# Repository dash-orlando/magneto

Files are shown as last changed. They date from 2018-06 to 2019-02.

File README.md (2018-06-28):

# magneto
PD3D Original Project: El Magnito Bandito

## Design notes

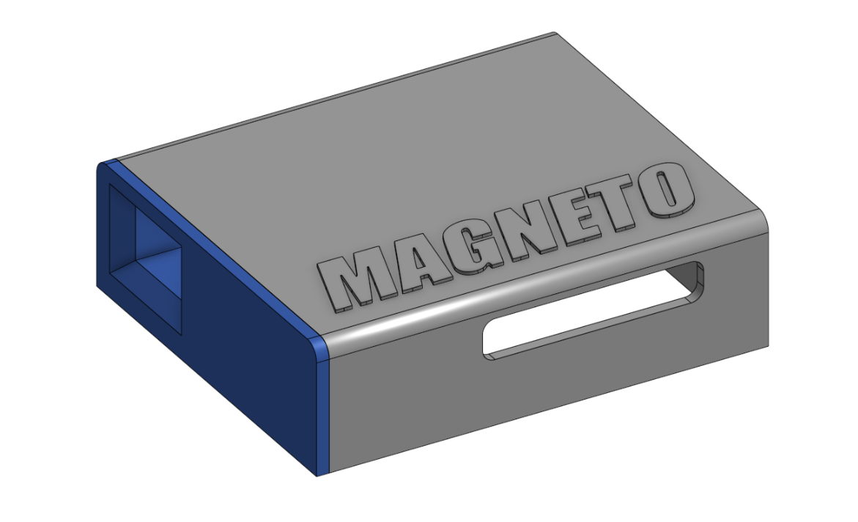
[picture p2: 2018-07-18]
Hardware/wearables/necklace/box/electronics_box_v1.png

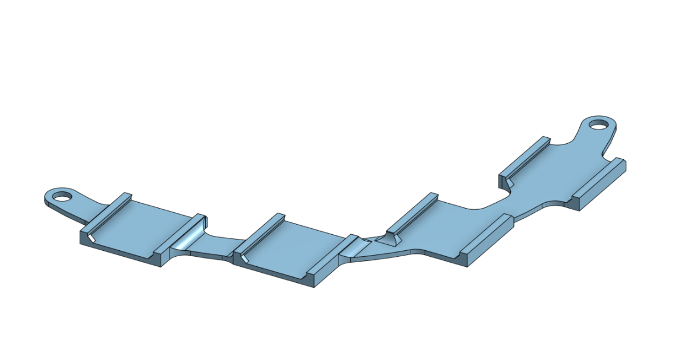
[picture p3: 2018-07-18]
Hardware/wearables/necklace/array/tunable_sensor_array_v1.png

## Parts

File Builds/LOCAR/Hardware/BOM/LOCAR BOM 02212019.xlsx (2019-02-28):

Part | Description |  | Source | Count | Price/unit
LED NeoPixel 12x5050 | Natural White LED ring for "Endoscope" |  | https://www.adafruit.com/product/2853 | 0 | $9.50
Rasberry Pi 3A+ | Controller for Magnetic Array |  | https://www.canakit.com/raspberry-pi-3-model-a-plus.html?cid=usd&src=raspberrypi | 0 | $25
Pi Camera | For "Laparoscope" |  | https://www.amazon.com/Raspberry-Pi-Camera-Module-Megapixel/dp/B01ER2SKFS?s=electronics | 0 | $24.90
Pi Camera Extension Cable | 1 meter |  | https://www.adafruit.com/product/2143 | 0 | $3.95
Power Supply | 5V 10A |  | https://www.amazon.com/dp/B00J3MHTYG/ref=nav_timeline_asin?_encoding=UTF8&th=1 | 2 | $10.99
M3 Inserts | 240-M3-BR M3-0.5 |  | https://www.amazon.com/240-M3-BR-M3-0-5-Flush-Press-Insert/dp/B06XGXFM21 | 1 | $14.50
10.1" Screen | for RAPID |  | https://www.amazon.com/Raspberry-Screen-10-1-IPS-SunFounder/dp/B07FZZ95WN?s=electronics | 1 | $110.00
Power Supply | 500W+ ATX style power supply | Needed to power the LOCAR | https://www.amazon.com/Corsair-Bronze-Certified-Modular-CP-9020102-NA/dp/B01B72W0A2 | 1.00 | $59.99

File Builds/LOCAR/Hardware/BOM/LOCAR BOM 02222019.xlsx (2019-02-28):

Account PI | Account Number | Project | Part | Description | Justification | Source | Count | Price/unit
Fluvio Lobo | 64018456 | EMGF - PCD | LED NeoPixel 12x5050 | Natural White LED ring for "Endoscope" |  | https://www.adafruit.com/product/2853 | 0.00 | $9.50 | $0.00
Fluvio Lobo | 64018456 | EMGF - PCD | Rasberry Pi 3A+ | Controller for Magnetic Array |  | https://www.canakit.com/raspberry-pi-3-model-a-plus.html?cid=usd&src=raspberrypi | 0.00 | $25.00 | $0.00
Fluvio Lobo | 64018456 | EMGF - PCD | Mount for 7" Touchscreen |  |  | https://www.amazon.com/Case-Official-Raspberry-Touchscreen-Display/dp/B01HV97F64 | 0.00 | $27.99 | $0.00
Fluvio Lobo | 64018456 | EMGF - PCD | Pi Camera | For "Laparoscope" |  | https://www.amazon.com/Raspberry-Pi-Camera-Module-Megapixel/dp/B01ER2SKFS?s=electronics | 0.00 | $24.90 | $0.00
Fluvio Lobo | 64018456 | EMGF - PCD | Pi Camera Extension Cable | 1 meter |  | https://www.adafruit.com/product/2143 | 0.00 | $3.95 | $0.00
Fluvio Lobo | 64018456 | EMGF - PCD | Power Supply | 5V 10A |  | https://www.amazon.com/dp/B00J3MHTYG/ref=nav_timeline_asin?_encoding=UTF8&th=1 | 0.00 | $10.99 | $0.00
Fluvio Lobo | 64018456 | EMGF - PCD |  |  |  |  |  |  | $0.00
Fluvio Lobo | 64018456 | EMGF - PCD | Power Supply | 500W+ ATX style power supply | Needed to power the LOCAR | https://www.amazon.com/Corsair-Bronze-Certified-Modular-CP-9020102-NA/dp/B01B72W0A2 | 1.00 | $59.99 | $59.99
Fluvio Lobo | 64018456 | EMGF - PCD | Power Dist. PCB | Custom PCB for power distribution | Needed to distribute power to each individual LOCAR component | Oshpark | 0.00 | $20.00 | $0.00
Fluvio Lobo | 64018456 | EMGF - PCD | Power Supply Cable | ATX Power Supply Connector - Right angle THT | Needed to assemble Power Dist. PCB | https://www.amazon.com/ATX-Power-Supply-Connector-Right/dp/B004G4ZFY2 | 4.00 | $2.95 | $11.80
Fluvio Lobo | 64018456 | EMGF - PCD | M3 Inserts | 240-M3-BR M3-0.5 |  | https://www.amazon.com/240-M3-BR-M3-0-5-Flush-Press-Insert/dp/B06XGXFM21 | 1.00 | $14.50 | $14.50
Fluvio Lobo | 64018456 | EMGF - PCD | 10.1" Screen | Raspberry Pi Screen | Needed to interface the Pi OS | https://www.amazon.com/Raspberry-Screen-10-1-IPS-SunFounder/dp/B07FZZ95WN?s=electronics | 1.00 | $110.00 | $110.00
Fluvio Lobo | 64018456 | EMGF - PCD | Plastic Spool | White | Needed to print parts | https://www.amazon.com/HATCHBOX-3D-Filament-Dimensional-Accuracy/dp/B00J0GMMP6?hvadid=312157487430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 | 1.00 | $20.00 | $20.00
Fluvio Lobo | 64018456 | EMGF - PCD | Plastic Spool | Silver | Needed to print parts | https://www.amazon.com/HATCHBOX-3D-Filament-Dimensional-Accuracy/dp/B00J0ECR5I | 1.00 | $20.00 | $20.00
Fluvio Lobo | 64018456 | EMGF - PCD | Plastic Spool | Black | Needed to print parts | https://www.amazon.com/HATCHBOX-3D-Filament-Dimensional-Accuracy/dp/B00MEZEEJ2?s=industrial | 1.00 | $20.00 | $20.00
 |  |  |  |  |  |  |  | Total = | $216.29

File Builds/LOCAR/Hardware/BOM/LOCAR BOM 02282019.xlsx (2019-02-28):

Part | Description | Justification | Source | Count | Price/unit
Right Angle Male Pins | Right Angle Male Pins | Needed to assemble the daisy-hub modules | https://www.amazon.com/Simpo-2-54mm-Connector-Plastic-Gold-plated/dp/B07BRZC6C6?hvadid=241935719665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 | 2.00 | $14.99 | $29.98
Female Header Pins | Female Header Pins | Needed to stack daisy-hub prototypes | https://www.amazon.com/Hilitchi-2-54mm-Arduino-Stackable-Assortment/dp/B01IPA8JZY?s=gateway | 2.00 | $9.99 | $19.98
 |  |  |  |  | Total = | $49.96

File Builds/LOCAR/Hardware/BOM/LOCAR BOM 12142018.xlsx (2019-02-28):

Part | Description | Justification | Source | Count | Price/unit
LED NeoPixel 12x5050 | Natural White LED ring for "Endoscope" |  | https://www.adafruit.com/product/2853 | 2.00 | $9.50 | $19.00
Rasberry Pi 3A+ | Controller for Magnetic Array |  | https://www.canakit.com/raspberry-pi-3-model-a-plus.html?cid=usd&src=raspberrypi | 3.00 | $25.00 | $75.00
Mount for 7" Touchscreen |  |  | https://www.amazon.com/Case-Official-Raspberry-Touchscreen-Display/dp/B01HV97F64 | 2.00 | $27.99 | $55.98
Pi Camera | For "Laparoscope" |  | https://www.amazon.com/Raspberry-Pi-Camera-Module-Megapixel/dp/B01ER2SKFS?s=electronics | 2.00 | $24.90 | $49.80
Pi Camera Extension Cable | 1 meter |  | https://www.adafruit.com/product/2143 | 2.00 | $3.95 | $7.90
Power Supply | 5V 10A |  | https://www.amazon.com/dp/B00J3MHTYG/ref=nav_timeline_asin?_encoding=UTF8&th=1 | 2.00 | $10.99 | $21.98
 |  |  |  |  |  | $0.00
Power Supply | 500W+ ATX style power supply | Needed to power the LOCAR | https://www.amazon.com/Corsair-Bronze-Certified-Modular-CP-9020102-NA/dp/B01B72W0A2 | 1.00 | $59.99 | $59.99
Power Dist. PCB | Custom PCB for power distribution | Needed to distribute power to each individual LOCAR component | Oshpark | 1.00 | $20.00 | $20.00
 | ATX Power Supply Connector - Right angle THT | Needed to assemble Power Dist. PCB | https://www.amazon.com/ATX-Power-Supply-Connector-Right/dp/B004G4ZFY2 | 1.00 | $2.95 | $2.95
 |  |  |  |  | Total = | $312.60

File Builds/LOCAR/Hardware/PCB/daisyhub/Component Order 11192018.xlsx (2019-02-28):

Account PI | Account Number | Account Name | Component | ID | Description | Justification | Link | Unit Cost | Quantity | Total Cost | Ordered | Delivered
Jack Stubbs |  |  | Jumper Cables |  | 4 pin, female to female jumper cables | Needed to connect daisy-pair modules | https://www.amazon.com/FEBNISCTE-Female-Jumper-Cable-Printer/dp/B00KWA1UWK?s=electronics | $9.99 | 2.00 | $19.98
 |  |  | Female Headers |  | Assortment of female headers | Needed to connect IMUs at certain height | https://www.amazon.com/Glarks-Connector-Assortment-Stackable-Breakaway/dp/B07CWSXY7P?s=electronics | $12.85 | 2.00 | $25.70
 |  |  | Right-angle, male headers |  | Right-angle | Needed to connect IMU pair modules | https://www.amazon.com/Saim-10PCS-2-54mm-Single-Headers/dp/B00899WOXK?s=electronics | $5.55 | 2.00 | $11.10
 |  |  | Straight, male headers |  | Straight | Needed to connect IMUs close to the surface of the breakout | https://www.amazon.com/Breakaway-Header-Straight-Connector-Prototype/dp/B07BXDYTBP?s=electronics | $8.99 | 1.00 | $8.99
 |  |  | LED |  | 5V, 3 mm |  | https://www.mouser.com/ProductDetail/Kingbright/WP710A10ID5V | $0.41 | 25.00 | $10.35
 |  |  | LED |  | 5V, 3 mm |  | https://www.mouser.com/ProductDetail/?qs=jBF9H7RTBaQ2jkR1uoa79Q%3d%3d | $0.41 | 25.00 | $10.35
 |  |  | LED |  | 5V, 3 mm |  | https://www.mouser.com/ProductDetail/Kingbright/WP710A10YD5V | $0.41 | 25.00 | $10.35
 |  |  |  |  |  |  |  |  | Total | $96.82

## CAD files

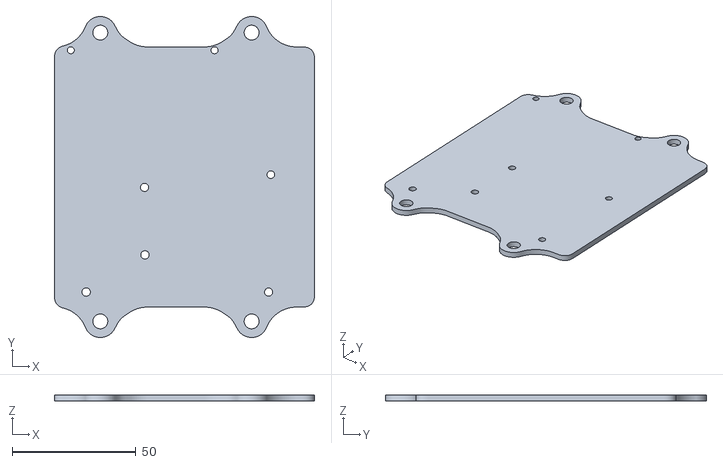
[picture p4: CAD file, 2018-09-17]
Builds/LOCAR/Hardware/6MAG_arduino_plate.stl
105.0 x 129.5 x 2.50

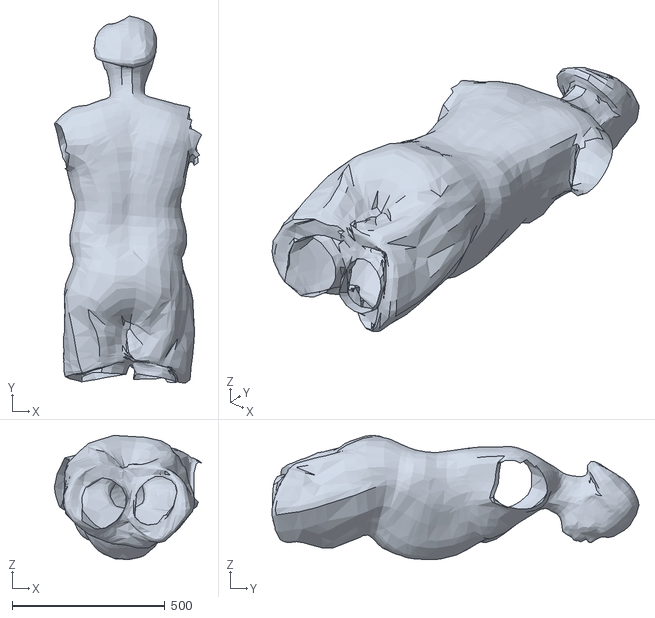
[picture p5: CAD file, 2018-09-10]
Builds/LOCAR/Software/Windows/Python 2.7/SP_PH02_Torso.obj
482.9 x 1202.6 x 406.8

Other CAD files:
Software/Python/Steth Edition/SP_PH02_Torso_Inverted (ASCII).stl
Builds/LOCAR/Software/Windows/Python 2.7/SP_PH02_Torso (BIN).stl
Builds/LOCAR/Software/Windows/Python 2.7/SP_PH02_Torso (ASCII).stl

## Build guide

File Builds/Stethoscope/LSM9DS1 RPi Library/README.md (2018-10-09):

SparkFun LSM9DS1 RaspberryPI Library
===

68747470733a2f2f63646e2e737061726b66756e2e636f6d2f2f6173736574732f70617274732f312f302f352f332f332f31333238342d30322e6a7067

[LSM9DS1 Breakout Board (SEN-13284)](https://www.sparkfun.com/products/13284)

Port [SparkFun_LSM9DS1_Arduino_Library](https://github.com/sparkfun/SparkFun_LSM9DS1_Arduino_Library) to Raspberry Pi

This library supports only I2C.

## Requirement

* [WiringPi](http://wiringpi.com/)

## Install

```
$ git clone https://github.com/akimach/LSM9DS1_RaspberryPi_Library.git
$ cd LSM9DS1_RaspberryPi_Library
$ make
$ sudo make install
```

## Python example

```
$ cd ./example
$ sudo python LSM9DS1_Basic_I2C.py
```

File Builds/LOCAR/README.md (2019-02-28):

# LOCAR
_**LOCAR**_, or the _**Location-based Trocar or Laparoscopic Trainer**_, is a cost-effective system for the live position tracking of surgical end-effectors.

> **NOTE** The latest versions of **LOCAR** are located in the _**locar**_ branch of the _**magneto**_ repository

## INSTALLATION
### Python 2.7
1. Install the following requirements
```
sudo pip install numpy
sudo pip install scipy
sudo apt-get install python-scipy
```

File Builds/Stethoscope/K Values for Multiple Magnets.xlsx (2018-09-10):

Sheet: Big Magnet
BIG MAGNET
H^2 | x | K | Hy^2 | y | K
6.86 | 0.075 | 1.220932617e-06 | 6.8121 | 0.075 | 1.212407446e-06
2.87 | 0.085 | 1.08241911e-06 | 2.8561 | 0.085 | 1.077176732e-06
1.31 | 0.095 | 9.629703767e-07 | 1.2769 | 0.095 | 9.386388351e-07
Taking Entire Norm |  | 1.088774035e-06 | Setting Hx=Hz=0 |  | 1.076074338e-06

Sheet: Small Magnet
SMALL MAGNET
H_x | H_y | H_z | x | y | z
0.19 | 0 | 0.83 | 0 | 0.075 | 0
K-Value |  |  |  |  | 1.290344238e-07

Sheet: Spherical Magnet
SPEHRICAL MAGNET
H^2 | x | K | Hy^2 | y | K
0.995 | 0.075 | 1.77088623e-07 | 0.996004 | 0.075 | 1.772673135e-07
0.64 | 0.085 | 2.4137569e-07 | 0.633616 | 0.085 | 2.389679675e-07
0.435 | 0.095 | 3.197649724e-07 | 0.42575625 | 0.095 | 3.129699668e-07
Taking Entire Norm |  | 2.460764285e-07 | Setting Hx=Hz=0 |  | 2.430684159e-07

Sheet: Small Magnet (with hole)
SMALL MAGNET (W\HOLE)
H_x | H_y | H_z | x | y | z
0.07 | 0.07 | 1.02 | 0 | 0.075 | 0
K-Value |  |  |  |  | 1.869130371e-07

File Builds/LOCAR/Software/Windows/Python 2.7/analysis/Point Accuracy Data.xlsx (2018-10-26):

 | Xm | Ym | Zm | Xe | Ye | Ze | Length | milliseconds to solution
No Tool | 11.791 | -135.68 | -430.562 | 3.488 | -40.137 | -127.368 | 318 | 0.021
 | 44.026 | -205.633 | -411.084 | 13.706 | -64.017 | -127.977 | 318 | 0.046
 | 13.39 | -262.575 | -389.993 | 4.337 | -85.047 | -126.316 | 318 | 0.05
 | 73.483 | -68.387 | -435.096 | 21.151 | -19.684 | -125.236 | 318 | 0.053
 | -8.5 | -55.943 | -457.334 | -2.634 | -17.338 | -141.74 | 318 | 0.05
 | 118.128 | -221.371 | -396.837 | 38.119 | -71.436 | -128.058 | 318 | 0.051
 | 35.189 | -392.242 | -217.09 | 10.305 | -114.866 | -63.574 | 318 | 0.052
 | 53.69 | -323.923 | -324.836 | 16.725 | -100.902 | -101.186 | 318 | 0.05
 | 0.882 | -297.198 | -345.54 | 0.267 | -89.837 | -104.449 | 318 | 0.049
 | -48.98 | -313.519 | -323.668 | -14.617 | -93.564 | -96.593 | 318 | 0.05
 | -40.418 | -106.73 | -450.539 | -12.764 | -33.704 | -142.275 | 318 | 0.05
 | 11.521 | 70.356 | -437.562 | 3.257 | 19.89 | -123.701 | 318 | 0.049
 | -41.873 | -323.034 | -334.576 | -13.357 | -103.045 | -106.726 | 318 | 0.05
 | 72.113 | -103.806 | -436.701 | 21.672 | -31.196 | -131.239 | 318 | 0.05
 | -40.18 | -152.054 | -449.781 | -13.364 | -50.575 | -149.603 | 318 | 0.052
 | 88.244 | -92.452 | -432.499 | 26.022 | -27.262 | -127.535 | 318 | 0.044
 | -129.119 | -84.686 | -421.646 | -37.678 | -24.712 | -123.04 | 318 | 0.047
 | -106.666 | -119.185 | -429.583 | -32.669 | -36.503 | -131.569 | 318 | 0.047
 | -78.684 | -142.069 | -418.498 | -22.945 | -41.428 | -122.037 | 318 | 0.045
 | 32.752 | -72.097 | -435.967 | 9.247 | -20.355 | -123.087 | 318 | 0.05
 | 15.918 | -112.405 | -428.539 | 4.5 | -31.776 | -121.143 | 318 | 0.043
 | 22.485 | -226.434 | -381.124 | 6.377 | -64.216 | -108.086 | 318 | 0.049
 | 43.544 | 30.685 | -435.418 | 11.978 | 8.441 | -119.772 | 318 | 0.046
 | -29.896 | -316.387 | -335.349 | -9.319 | -98.619 | -104.529 | 318 | 0.048
 | -13.988 | -355.039 | -281.021 | -4.169 | -105.814 | -83.754 | 318 | 0.045
 | -2.207 | -177.358 | -429.925 | -0.698 | -56.088 | -135.96 | 318 | 0.046
 | 11.226 | -145.789 | -431.476 | 3.39 | -44.026 | -130.3 | 318 | 0.047
 | -15.919 | -187.24 | -416.46 | -4.839 | -56.92 | -126.602 | 318 | 0.045
 | 30.017 | -122.881 | -426.986 | 8.582 | -35.134 | -122.084 | 318 | 0.048
 | 111.89 | -64.447 | -416.042 | 30.211 | -17.401 | -112.333 | 318 | 0.048
 | 93.979 | 47.633 | -426.244 | 25.914 | 13.134 | -117.535 | 318 | 0.046
 | 144.263 | 64.079 | -420.36 | 42.095 | 18.698 | -122.658 | 318 | 0.047
 | 128.704 | 20.196 | -435.387 | 38.646 | 6.064 | -130.733 | 318 | 0.046
 | 35.203 | 5.691 | -433.853 | 9.487 | 1.534 | -116.922 | 318 | 0.045
 | 23.279 | -101.283 | -434.158 | 6.697 | -29.136 | -124.894 | 318 | 0.047
 | -81.417 | -126.108 | -424.124 | -23.87 | -36.973 | -124.345 | 318 | 0.044
 | -40.877 | -148.342 | -435.77 | -12.749 | -46.267 | -135.914 | 318 | 0.045
 | 27.348 | -183.169 | -416.475 | 8.268 | -55.376 | -125.909 | 318 | 0.047
 | -46.981 | -42.877 | -442.12 | -13.534 | -12.351 | -127.361 | 318 | 0.048
 | -24.726 | -145.052 | -440.523 | -7.797 | -45.737 | -138.904 | 318 | 0.046
 | -54.388 | -166.254 | -413.258 | -15.847 | -48.442 | -120.412 | 318 | 0.047
 | 38.589 | -37.22 | -437.32 | 10.737 | -10.356 | -121.683 | 318 | 0.046
 | 2.676 | -139.262 | -422.801 | 0.764 | -39.779 | -120.768 | 318 | 0.047
 | 114.945 | -12.355 | -423.011 | 31.592 | -3.396 | -116.26 | 318 | 0.046
 | 2.491 | -86.519 | -417.186 | 0.632 | -21.945 | -105.817 | 318 | 0.046
 | 207.918 | -177.162 | -350.607 | 59.157 | -50.406 | -99.755 | 318 | 0.047
 | 152.829 | -13.231 | -409.746 | 41.749 | -3.614 | -111.933 | 318 | 0.046
 | 67.892 | -245.57 | -367.578 | 19.619 | -70.964 | -106.223 | 318 | 0.046
 | 28.39 | -126.567 | -420.371 | 7.868 | -35.079 | -116.508 | 318 | 0.047
 | 44.255 | -243.541 | -364.31 | 12.303 | -67.706 | -101.28 | 318 | 0.047
 | -5.605 | -289.303 | -331.712 | -1.556 | -80.302 | -92.074 | 318 | 0.046
 | -52.69 | -193.19 | -397.328 | -15.032 | -55.115 | -113.354 | 318 | 0.047
 | -100.554 | -233.97 | -367.093 | -28.983 | -67.439 | -105.81 | 318 | 0.047
 | -81.167 | -269.308 | -348.019 | -23.485 | -77.922 | -100.697 | 318 | 0.047
 | -87.173 | -258.012 | -350.972 | -24.772 | -73.32 | -99.737 | 318 | 0.045
 | -124.527 | -234.581 | -349.305 | -34.283 | -64.581 | -96.165 | 318 | 0.047
 | -100.678 | -315.033 | -275.066 | -26.252 | -82.146 | -71.724 | 318 | 0.047
 | -158.434 | -283.69 | -282.454 | -41.413 | -74.153 | -73.83 | 318 | 0.045
 | 42.369 | -398.35 | -115.912 | 10.061 | -94.593 | -27.525 | 318 | 0.048
 | 39.308 | -204.708 | -407.183 | 11.982 | -62.399 | -124.118 | 318 | 0.044
 | 57.747 | -130.26 | -438.532 | 17.921 | -40.425 | -136.096 | 318 | 0.046
 | 68.268 | -105.048 | -432.185 | 20.023 | -30.81 | -126.758 | 318 | 0.044
 | -25.019 | -134.94 | -431.035 | -7.431 | -40.079 | -128.023 | 318 | 0.048
 | 57.342 | -132.649 | -442.513 | 18.171 | -42.034 | -140.224 | 318 | 0.047
 | 16.322 | -108.801 | -444.551 | 4.988 | -33.252 | -135.864 | 318 | 0.046
 | 155.806 | 19.056 | -396.705 | 39.672 | 4.852 | -101.01 | 318 | 0.048
 | 264.134 | 162.349 | -135.275 | 15.824 | 9.726 | -8.104 | 318 | 0.048
 | -70.926 | -87.269 | -428.794 | -20.047 | -24.666 | -121.196 | 318 | 0.045
 | 32.626 | -156.443 | -423.985 | 9.728 | -46.647 | -126.421 | 318 | 0.046
 | 11.003 | -405.884 | -117.914 | 2.727 | -100.613 | -29.229 | 318 | 0.049
 | -119.689 | -227.291 | -363.041 | -34.107 | -64.769 | -103.452 | 318 | 0.046
 | -59.989 | -138.469 | -412.307 | -16.54 | -38.178 | -113.68 | 318 | 0.047
 | 94.751 | -73.51 | -425.228 | 26.553 | -20.601 | -119.167 | 318 | 0.046
 | 1.937 | -65.458 | -428.02 | 0.514 | -17.385 | -113.678 | 318 | 0.047
 | 64.279 | -77.389 | -428.926 | 17.883 | -21.53 | -119.328 | 318 | 0.047
 | 77.85 | 79.745 | -414.644 | 20.191 | 20.683 | -107.542 | 318 | 0.046
 | 70.97 | -3.589 | -448.756 | 21.298 | -1.077 | -134.67 | 318 | 0.046
 | -0.457 | -68.961 | -451.637 | -0.139 | -20.962 | -137.281 | 318 | 0.047
 | 145.3 | -150.801 | -417.763 | 46.425 | -48.183 | -133.479 | 318 | 0.045
 | 138.449 | -132.293 | -417.59 | 42.614 | -40.719 | -128.533 | 318 | 0.046
 | -45.319 | -291.637 | -355.316 | -14.119 | -90.858 | -110.697 | 318 | 0.047
 | -19.134 | -135.858 | -436.275 | -5.83 | -41.392 | -132.921 | 318 | 0.045
 | 78.256 | -318.984 | -326.526 | 24.524 | -99.962 | -102.325 | 318 | 0.048
 | 26.471 | -173.646 | -422.833 | 8.086 | -53.044 | -129.164 | 318 | 0.047
 | 42.097 | -316.378 | -321.875 | 12.564 | -94.427 | -96.067 | 318 | 0.046
 | 47.646 | -146.739 | -420.117 | 13.792 | -42.476 | -121.609 | 318 | 0.048
 | 91.583 | 40.157 | -420.893 | 24.263 | 10.639 | -111.505 | 318 | 0.045
 | 9.599 | -110.055 | -428.923 | 2.707 | -31.04 | -120.973 | 318 | 0.048
 | 72.907 | -207.401 | -391.995 | 21.321 | -60.653 | -114.636 | 318 | 0.045
 | 126.971 | -76.323 | -412.815 | 34.911 | -20.985 | -113.505 | 318 | 0.046
 | 102.61 | 68.895 | -401.996 | 25.024 | 16.802 | -98.038 | 318 | 0.047
 | 104.376 | -267.367 | -348.038 | 30.8 | -78.897 | -102.702 | 318 | 0.048
 | 90.287 | -264.303 | -357.275 | 26.975 | -78.967 | -106.744 | 318 | 0.044
 | 95.778 | -57.925 | -436.764 | 28.227 | -17.071 | -128.719 | 318 | 0.048
 | 61.104 | -204.077 | -398.196 | 18.077 | -60.373 | -117.8 | 318 | 0.047
 | 18.263 | -143.042 | -431.772 | 5.505 | -43.117 | -130.149 | 318 | 0.047
 | 53.818 | -250.56 | -363.911 | 15.367 | -71.545 | -103.912 | 318 | 0.048
 | 15.88 | -7.123 | -431.835 | 4.195 | -1.882 | -114.093 | 318 | 0.047
 | 60.212 | -138.011 | -424.873 | 17.734 | -40.649 | -125.139 | 318 | 0.045
 | 82.638 | -43.384 | -446.56 | 25.035 | -13.143 | -135.286 | 318 | 0.047
 | -9.65 | -416.883 | -121.816 | -2.586 | -111.723 | -32.646 | 318 | 0.048
 | -58.815 | -404.706 | 164.802 | -16.396 | -112.821 | 45.942 | 318 | 0.047
 | -30.526 | -370.933 | 262.201 | -9.204 | -111.842 | 79.058 | 318 | 0.045
 | 37.62 | -116.039 | 431.693 | 10.952 | -33.782 | 125.676 | 318 | 0.047
 | -115.015 | -303.231 | 313.224 | -33.895 | -89.363 | 92.308 | 318 | 0.047
 | -0.423 | -237.288 | 397.37 | -0.132 | -74.252 | 124.344 | 318 | 0.047
 | -12.331 | -263.909 | 371.677 | -3.732 | -79.87 | 112.486 | 318 | 0.046
 | 44.773 | -309.974 | 307.504 | 12.334 | -85.394 | 84.713 | 318 | 0.047
 | -97.521 | -186.915 | 392.91 | -27.972 | -53.614 | 112.7 | 318 | 0.048
 | -84.173 | -214.812 | 366.893 | -22.413 | -57.199 | 97.694 | 318 | 0.045
 | -198.303 | -212.981 | 306.49 | -49.096 | -52.73 | 75.881 | 318 | 0.048
 | 251.143 | 87.217 | 198.071 | 10.249 | 3.559 | 8.083 | 318 | 0.048
 | 82.449 | -79.728 | 376.865 | 15.892 | -15.368 | 72.642 | 318 | 0.043
 | -76.897 | -176.247 | 374.149 | -18.768 | -43.016 | 91.316 | 318 | 0.046
 | -334.904 | -222.955 | 121.69 | -81.533 | -54.279 | 29.626 | 318 | 0.046
 | -349.406 | -215.184 | 124.504 | -90.3 | -55.612 | 32.177 | 318 | 0.043
 | -209.596 | -333.781 | 232.301 | -63.909 | -101.774 | 70.832 | 318 | 0.045
 | -17.465 | -382.524 | 104.497 | -3.473 | -76.061 | 20.778 | 318 | 0.045
 | -141.483 | -184.59 | 429.908 | -49.435 | -64.497 | 150.213 | 318 | 0.045
 | 37.943 | 141.739 | 416.121 | 10.597 | 39.586 | 116.219 | 318 | 0.046
 | 81.403 | 15.758 | 445.293 | 24.252 | 4.695 | 132.666 | 318 | 0.046
 | -36.825 | 91.897 | 409.705 | -9.042 | 22.565 | 100.601 | 318 | 0.047
 | -105.868 | 1.346 | 407.733 | -25.95 | 0.33 | 99.941 | 318 | 0.045
 | -93.474 | -3.148 | 399.788 | -21.077 | -0.71 | 90.149 | 318 | 0.047
 | -113.978 | -221.617 | 303.598 | -21.7 | -42.193 | 57.801 | 318 | 0.049
Tool Inserted | -113.675 | -171.167 | 317.368 | -18.063 | -27.199 | 50.431 | 318 | 0.045
 | -80.63 | -182.497 | 315.342 | -11.918 | -26.976 | 46.612 | 318 | 0.046
 | -71.765 | -158.771 | 326.732 | -10.134 | -22.419 | 46.136 | 318 | 0.048
 | -41.888 | -184.209 | 323.9 | -6.364 | -27.985 | 49.207 | 318 | 0.045
 | -31.206 | -222.142 | 293.653 | -4.352 | -30.977 | 40.949 | 318 | 0.047
 | -10.687 | -188.327 | 308.951 | -1.298 | -22.883 | 37.539 | 318 | 0.048
 | -7.664 | -209.08 | 275.166 | -0.614 | -16.738 | 22.029 | 318 | 0.047
 | -31.573 | -156.845 | 298.144 | -1.9 | -9.438 | 17.94 | 318 | 0.048
 | -10.916 | -186.922 | 268.721 | -0.317 | -5.434 | 7.812 | 318 | 0.048
 | -3.003 | -146.542 | 286.127 | -0.033 | -1.588 | 3.101 | 318 | 0.046
 | 8.136 | -186.365 | 265.124 | 0.155 | -3.549 | 5.049 | 318 | 0.046
 | 12.881 | -179.785 | 267.244 | 0.174 | -2.425 | 3.604 | 318 | 0.045
 | -73.962 | 6.338 | 263.902 | 11.832 | -1.014 | -42.218 | 318 | 0.048
 | -49.605 | 8.356 | 272.48 | 7.325 | -1.234 | -40.235 | 318 | 0.046
 | -3.918 | -83.947 | 279.669 | 0.349 | 7.468 | -24.879 | 318 | 0.047
 | -6.934 | -29.698 | 260.509 | 1.473 | 6.308 | -55.334 | 318 | 0.046
 | -15.519 | -30.354 | 246.798 | 4.289 | 8.389 | -68.211 | 318 | 0.051
 | -13.213 | -11.421 | 232.599 | 4.801 | 4.15 | -84.508 | 318 | 0.045
 | -12.157 | -39.292 | 227.768 | 4.546 | 14.693 | -85.17 | 318 | 0.047
 | -11.582 | -32.053 | 222.713 | 4.765 | 13.187 | -91.628 | 318 | 0.048
 | -2.601 | -15.488 | 213.457 | 1.263 | 7.523 | -103.686 | 318 | 0.049
 | -3.327 | -14.682 | 209.627 | 1.707 | 7.533 | -107.556 | 318 | 0.045
 | -3.742 | -15.714 | 202.593 | 2.113 | 8.873 | -114.401 | 318 | 0.046
 | -10.714 | -36.918 | 202.139 | 5.844 | 20.138 | -110.262 | 318 | 0.046
 | -11.135 | -37.332 | 194.198 | 6.743 | 22.605 | -117.59 | 318 | 0.049
 | -3.402 | -10.89 | 179.317 | 2.619 | 8.383 | -138.042 | 318 | 0.047
 | -42.893 | 9.596 | 175.909 | 32.334 | -7.234 | -132.606 | 318 | 0.048
 | -53.201 | 17.472 | 165.245 | 43.764 | -14.373 | -135.933 | 318 | 0.049
 | -53.342 | 32.74 | 158.267 | 46.325 | -28.434 | -137.449 | 318 | 0.048
 | -47.439 | 47.482 | 149.701 | 44.513 | -44.553 | -140.468 | 318 | 0.048
 | -37.772 | 51.562 | 133.935 | 43.166 | -58.925 | -153.059 | 318 | 0.048
 | -33.902 | 53.532 | 126.173 | 42.454 | -67.038 | -158.004 | 318 | 0.047
 | -18.205 | 39.306 | 122.046 | 26.497 | -57.21 | -177.638 | 318 | 0.049
At TPOS 1 | -16.711 | 38.524 | 121.332 | 24.678 | -56.891 | -179.179 | 318 | 0.046
 | -16.959 | 40.465 | 120.575 | 25.072 | -59.823 | -178.256 | 318 | 0.048
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

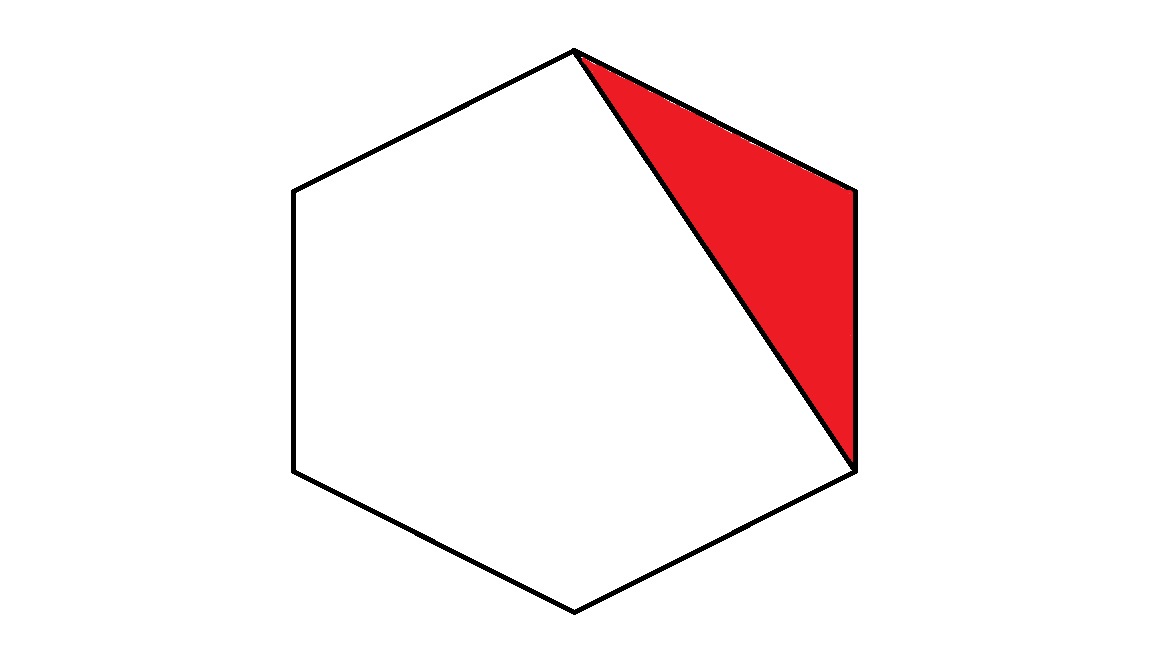
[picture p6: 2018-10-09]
Builds/Stethoscope/Python/Images/3.jpg

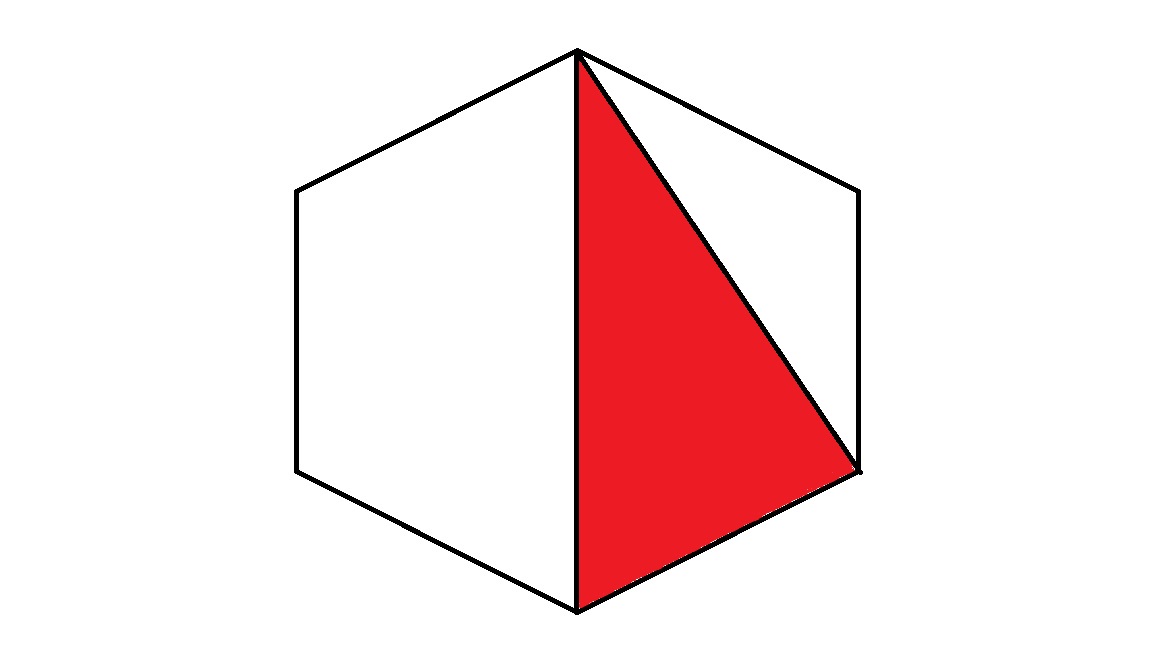
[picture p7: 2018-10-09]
Builds/Stethoscope/Python/Images/8.jpg

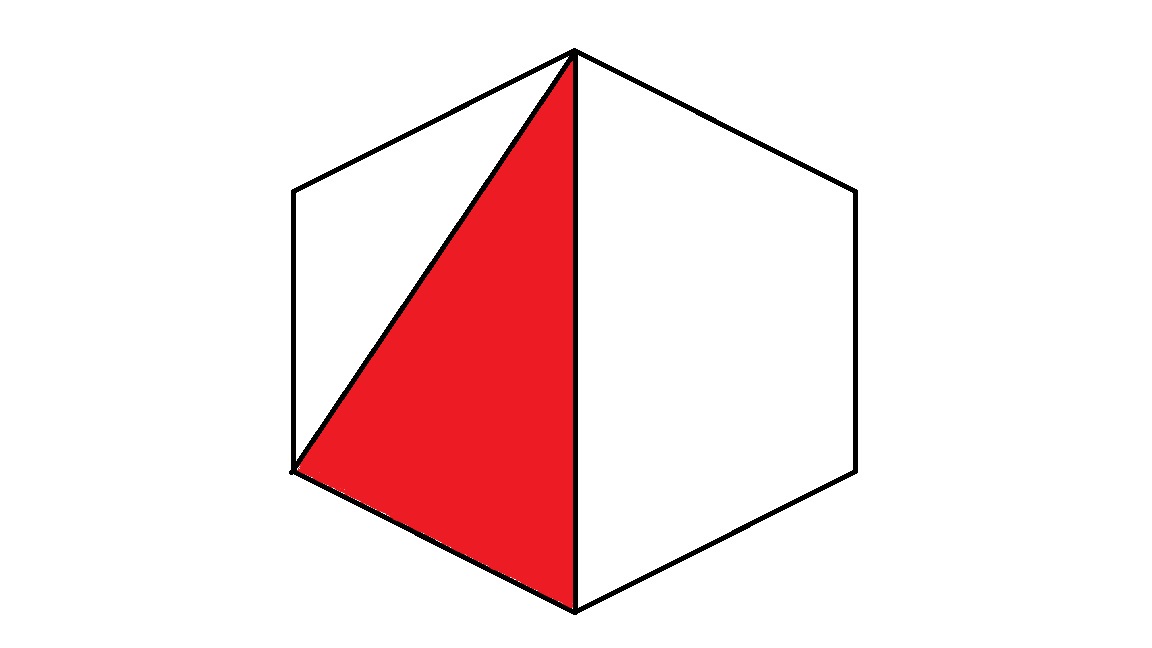
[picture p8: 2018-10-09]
Builds/Stethoscope/Python/Images/7.jpg

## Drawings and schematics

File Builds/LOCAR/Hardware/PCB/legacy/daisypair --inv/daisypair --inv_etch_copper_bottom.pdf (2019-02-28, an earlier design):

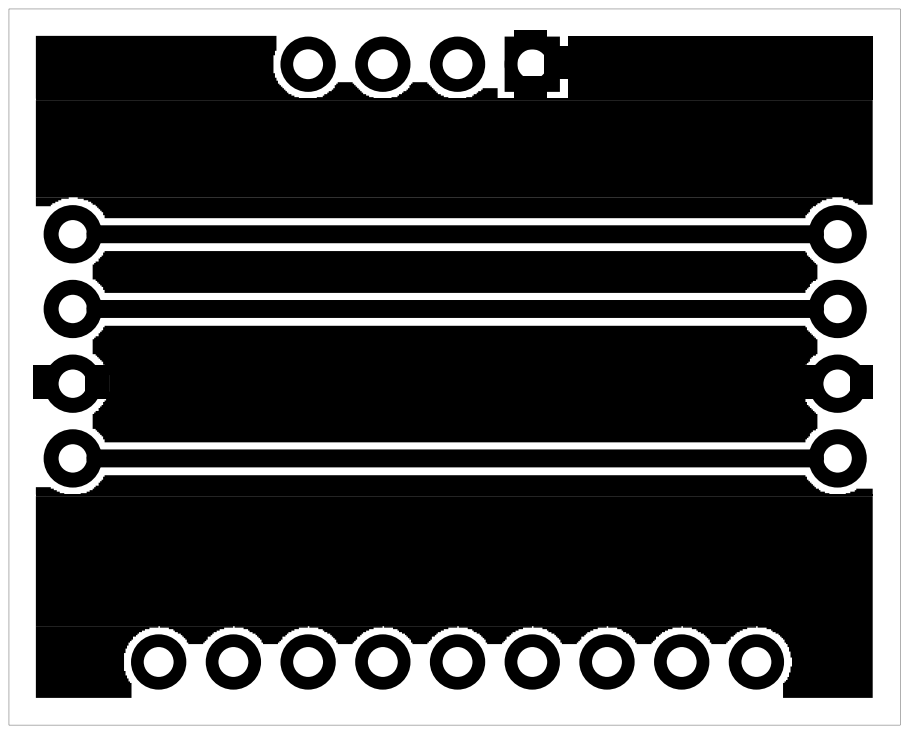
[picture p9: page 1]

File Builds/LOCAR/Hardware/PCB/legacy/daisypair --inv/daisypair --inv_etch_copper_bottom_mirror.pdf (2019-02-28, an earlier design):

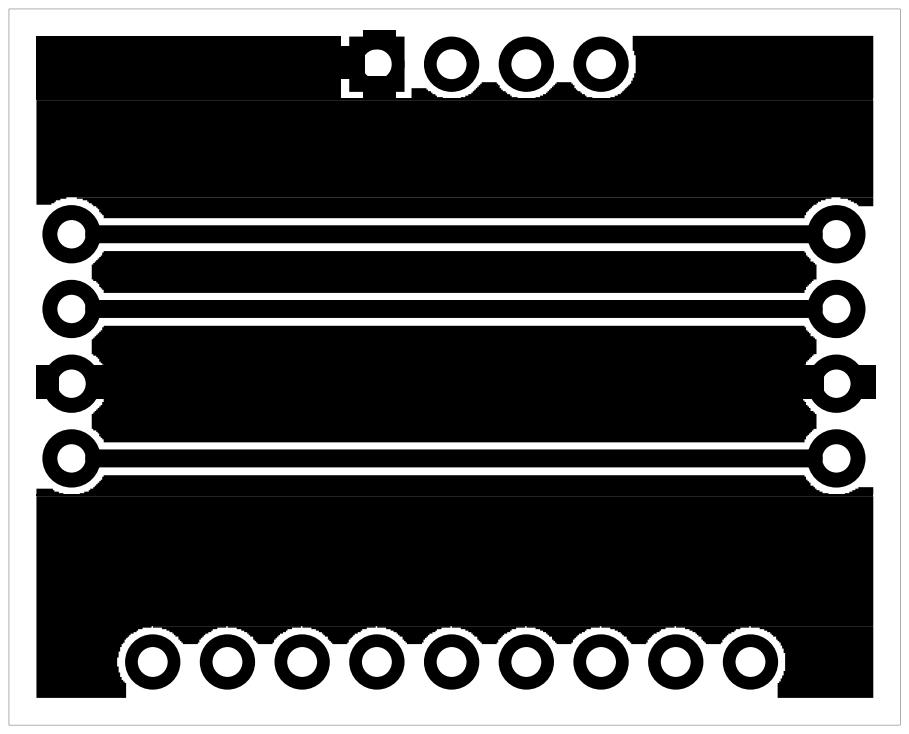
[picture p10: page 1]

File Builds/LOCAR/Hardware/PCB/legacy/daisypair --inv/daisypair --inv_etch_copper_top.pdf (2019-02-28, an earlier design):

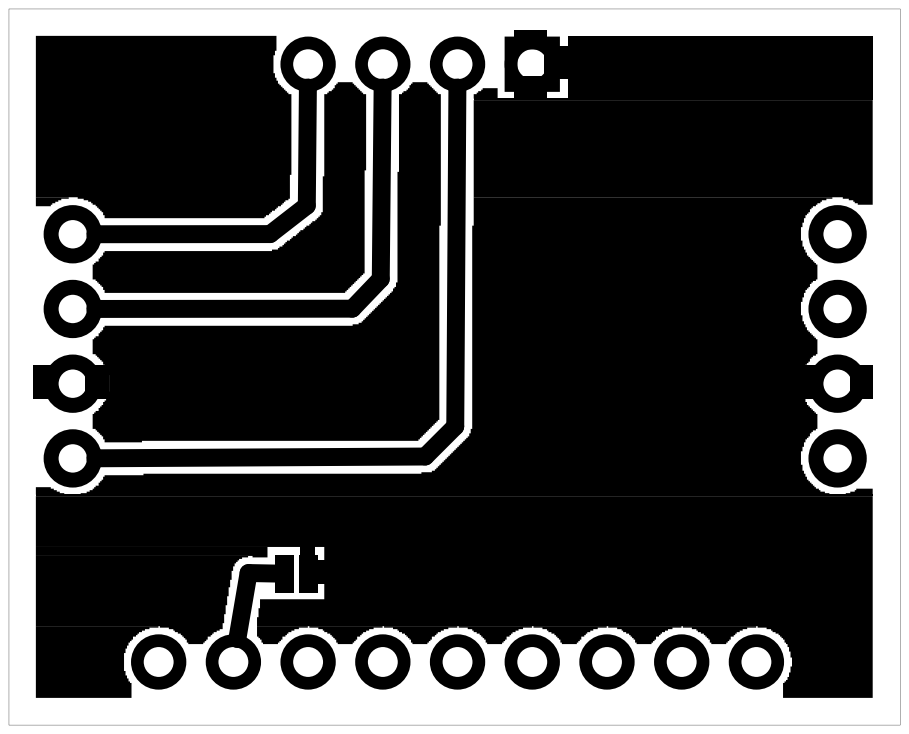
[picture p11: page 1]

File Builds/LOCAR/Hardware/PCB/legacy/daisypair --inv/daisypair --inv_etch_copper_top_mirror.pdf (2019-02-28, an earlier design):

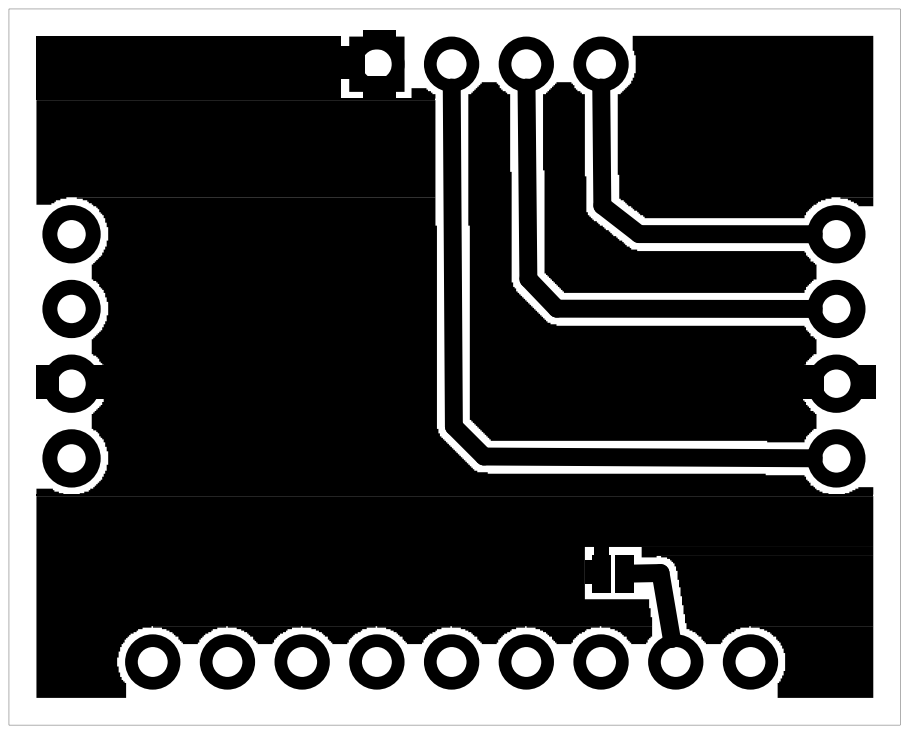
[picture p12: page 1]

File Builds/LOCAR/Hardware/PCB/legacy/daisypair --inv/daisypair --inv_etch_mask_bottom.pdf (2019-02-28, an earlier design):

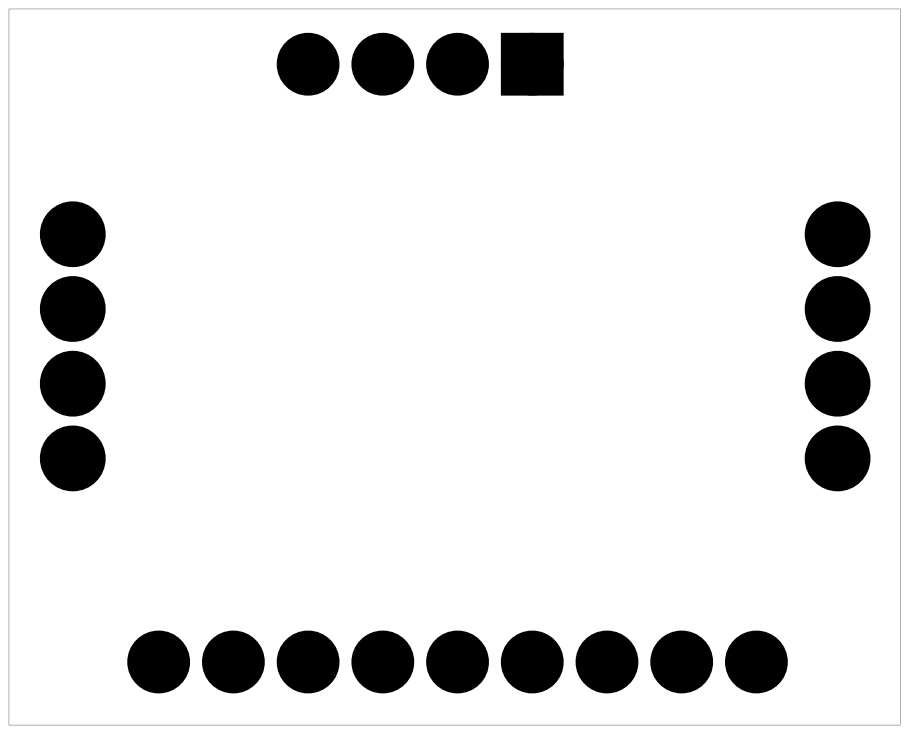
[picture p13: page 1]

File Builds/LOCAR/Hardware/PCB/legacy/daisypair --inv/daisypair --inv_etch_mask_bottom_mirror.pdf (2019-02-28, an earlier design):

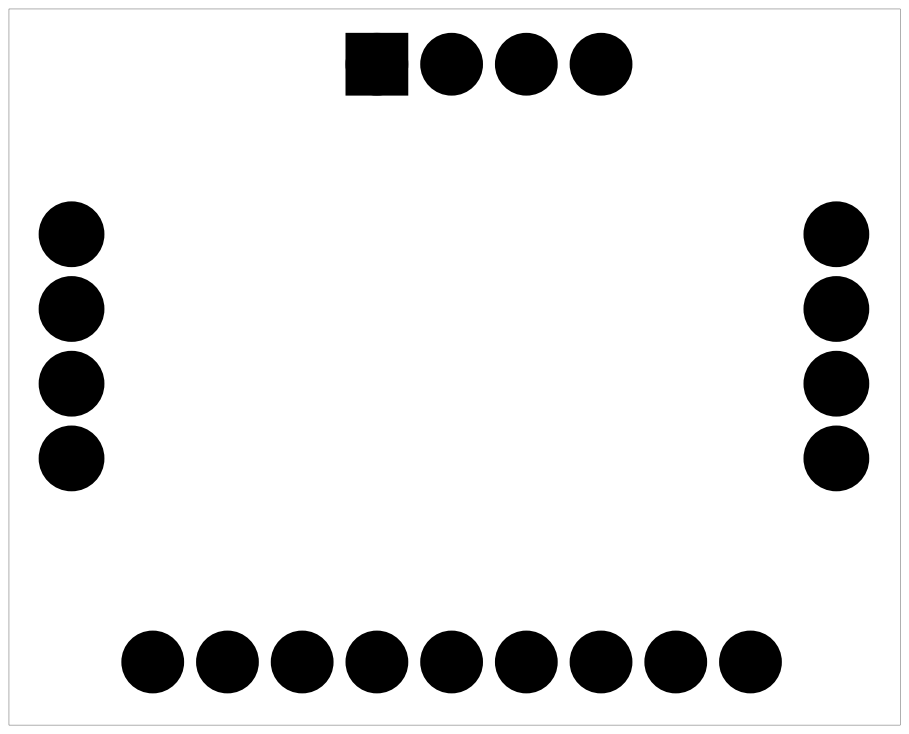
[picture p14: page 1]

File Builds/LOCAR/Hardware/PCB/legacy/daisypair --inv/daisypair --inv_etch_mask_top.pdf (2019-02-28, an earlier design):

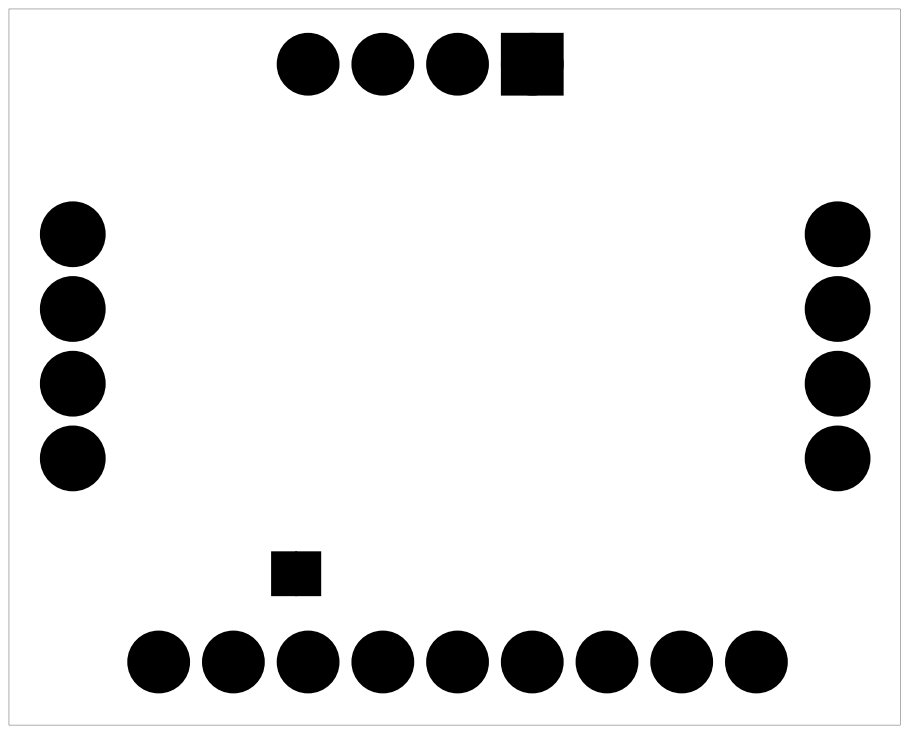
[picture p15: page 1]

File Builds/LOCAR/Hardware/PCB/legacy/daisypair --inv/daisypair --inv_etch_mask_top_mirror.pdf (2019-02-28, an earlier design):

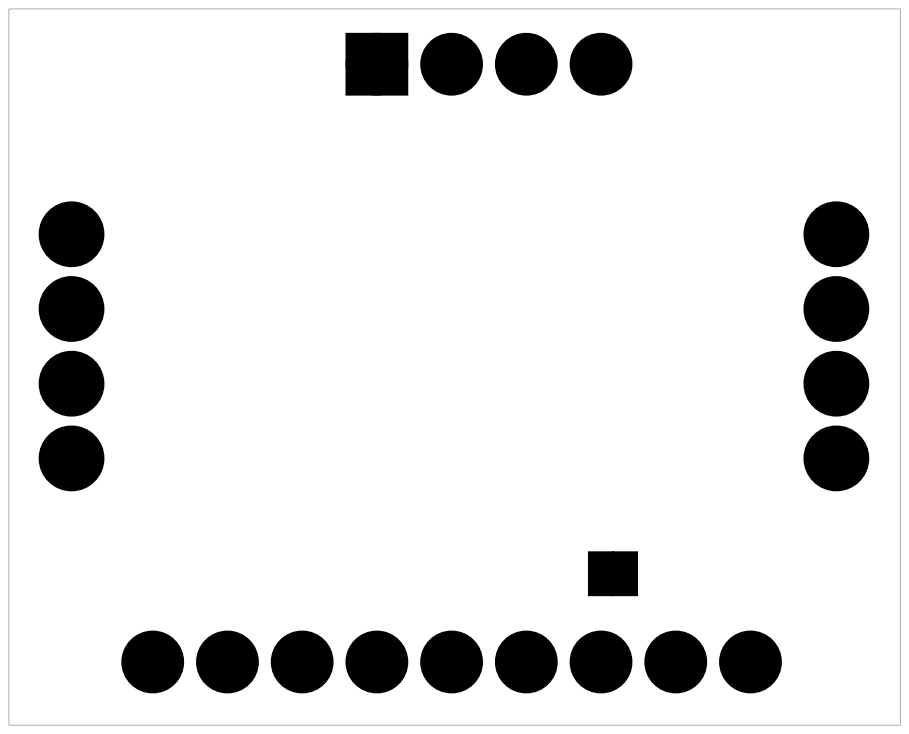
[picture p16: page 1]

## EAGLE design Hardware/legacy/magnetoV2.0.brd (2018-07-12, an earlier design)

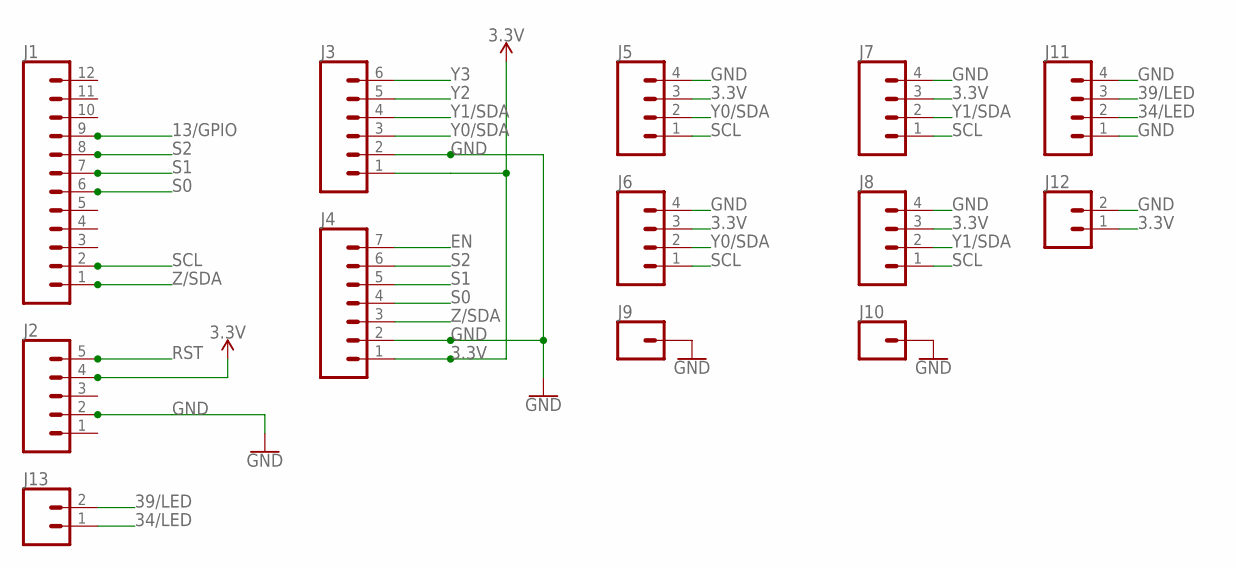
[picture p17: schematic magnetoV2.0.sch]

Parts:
J1: CONN_12; 1X12
J2: CONN_05; 1X05
J3: CONN_06SILK_FEMALE_PTH; 1X06
J4: CONN_07; 1X07
J5, J6, J7, J8, J11: CONN_04; 1X04
J9, J10: CONN_01; 1X01
J12, J13: CONN_02; 1X02

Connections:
3.3V: J2.4, J3.1, J4.1, J5.3, J6.3, J7.3, J8.3, J12.1
13/GPIO: J1.9
34/LED: J11.2, J13.1
39/LED: J11.3, J13.2
EN: J4.7
GND: J2.2, J3.2, J4.2, J5.4, J6.4, J7.4, J8.4, J9.1, J10.1, J11.1, J11.4, J12.2
RST: J2.5
S0: J1.6, J4.4
S1: J1.7, J4.5
S2: J1.8, J4.6
SCL: J1.2, J5.1, J6.1, J7.1, J8.1
Y0/SDA: J3.3, J5.2, J6.2
Y1/SDA: J3.4, J7.2, J8.2
Y2: J3.5
Y3: J3.6
Z/SDA: J1.1, J4.3

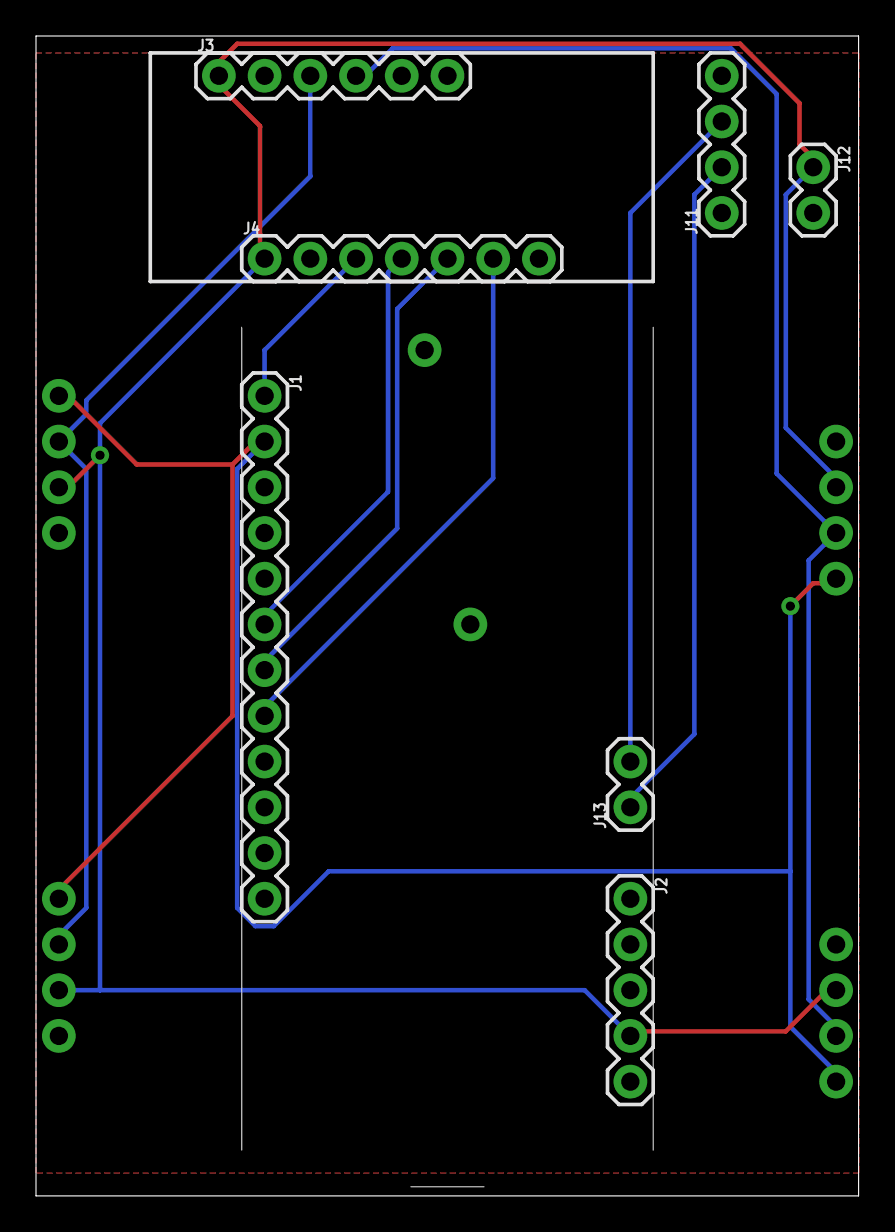
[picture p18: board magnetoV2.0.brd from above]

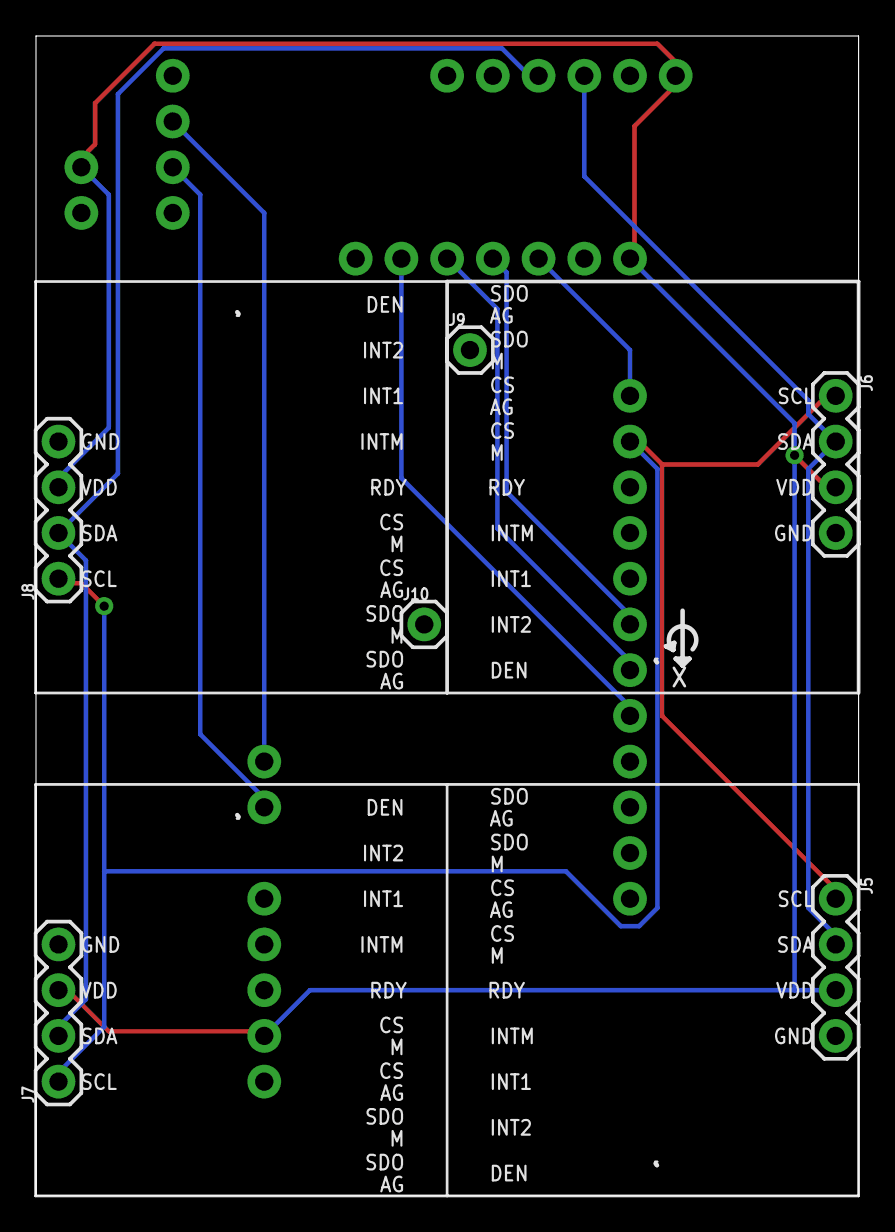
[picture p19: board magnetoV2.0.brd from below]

Board: 2 copper layers, 45.7 x 64.4 mm, 13 parts (6 on the bottom side), 11 nets.

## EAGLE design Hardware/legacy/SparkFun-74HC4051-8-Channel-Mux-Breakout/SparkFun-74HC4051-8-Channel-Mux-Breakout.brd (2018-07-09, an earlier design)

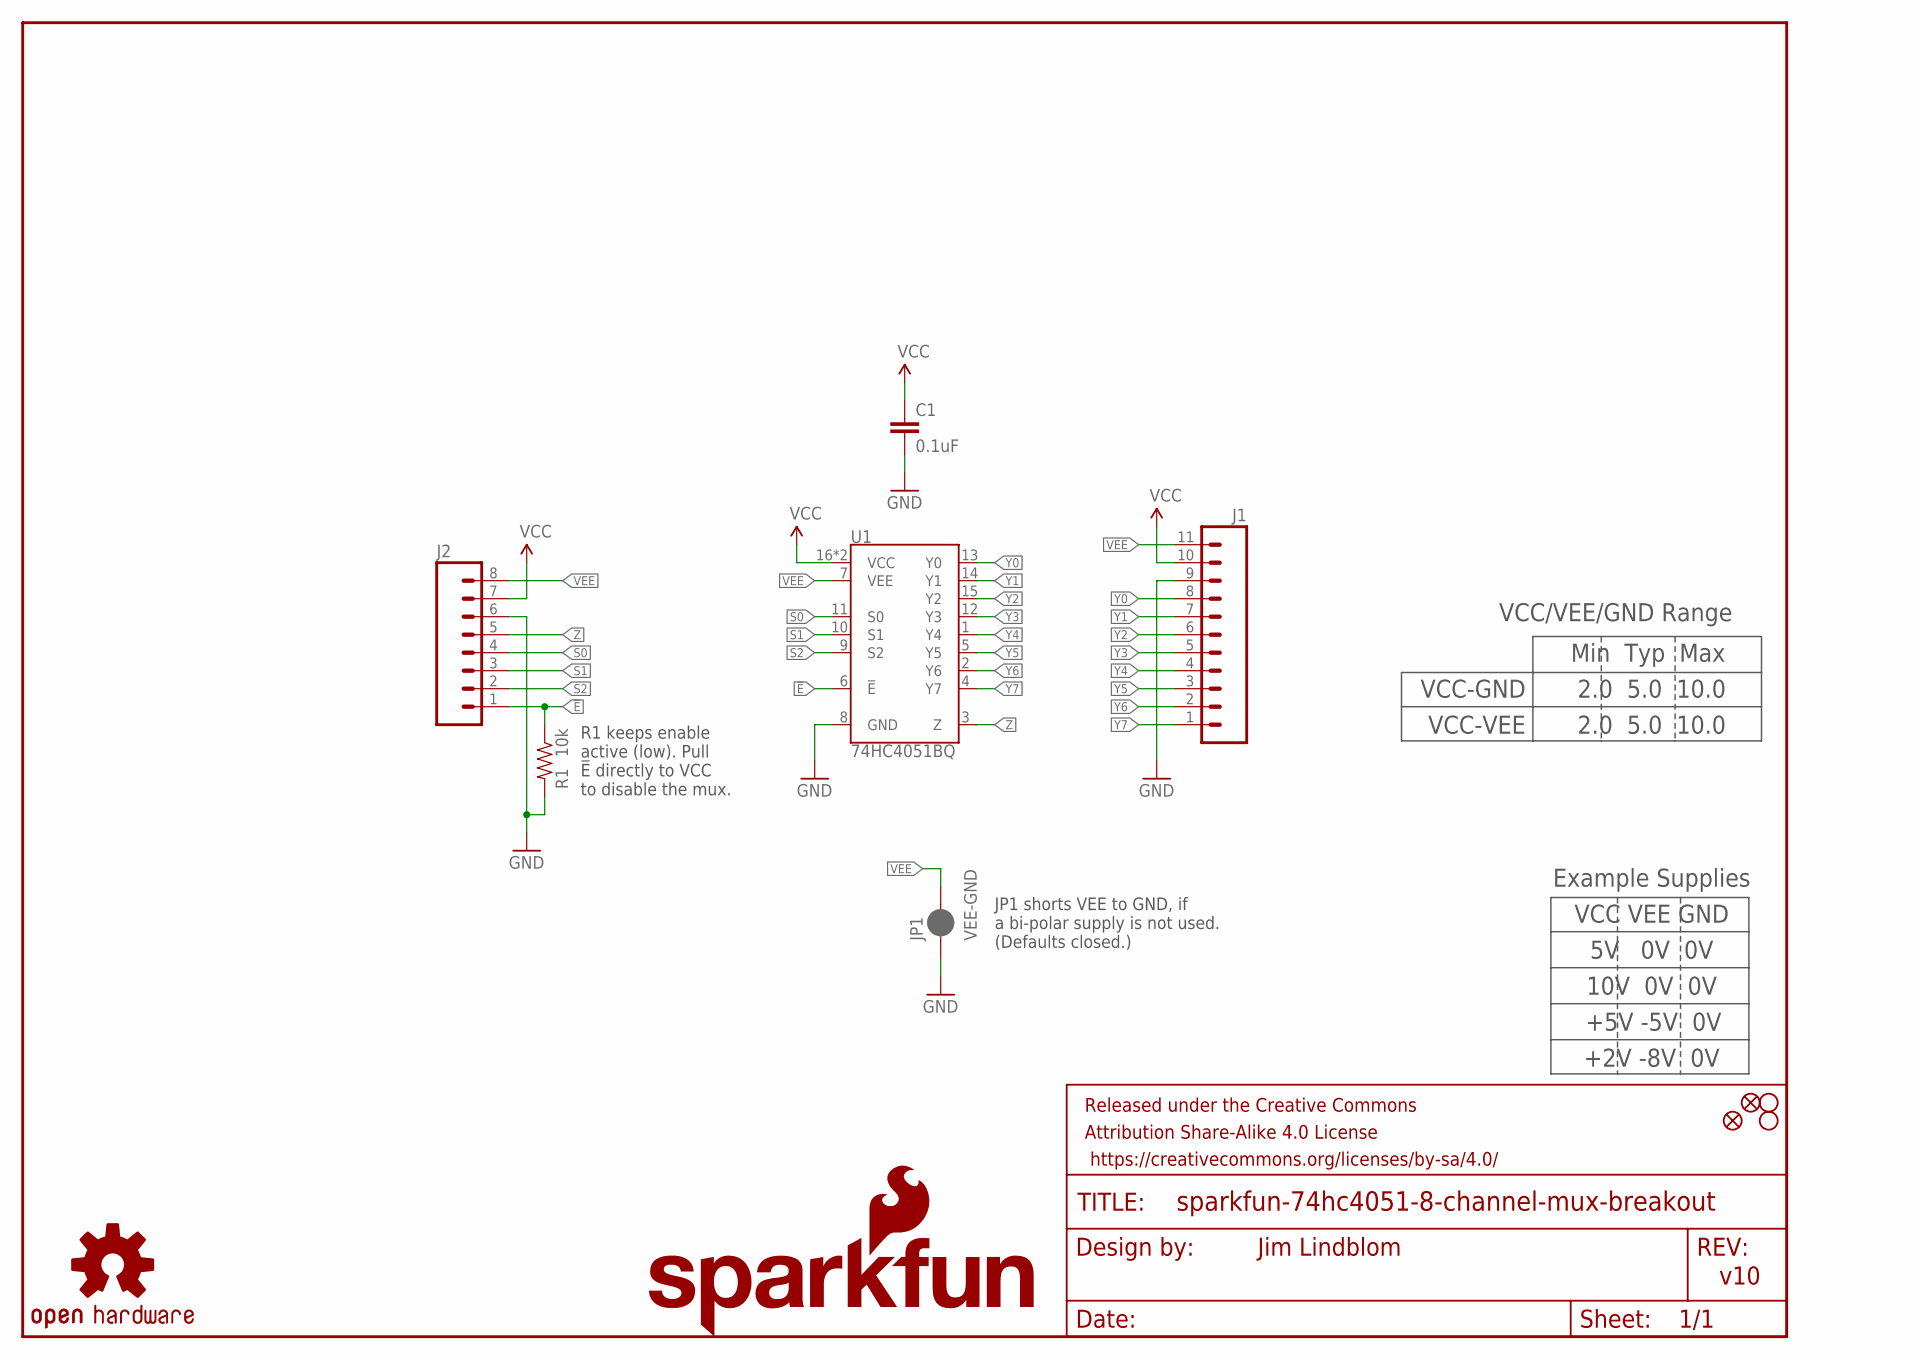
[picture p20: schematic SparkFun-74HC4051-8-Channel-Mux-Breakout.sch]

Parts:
C1: 0.1uF; 0603
FD1, FD2: FIDUCIAL1X2; FIDUCIAL-1X2
FRAME1: FRAME-LETTER; CREATIVE_COMMONS
H1, H2: STAND-OFF
J1: M11PTH; 1X11
J2: M08; 1X08_ROUND
JP1: VEE-GND; PAD-JUMPER-2-NC_BY_PASTE_NO_SILK
LOGO1: SFE_LOGO_FLAME.1_INCH; SFE_LOGO_FLAME_.1
LOGO2: OSHW-LOGOMINI; OSHW-LOGO-MINI
LOGO3: SFE_LOGO_NAME.1_INCH; SFE_LOGO_NAME_.1
R1: 10k; 0603
U1: 74HC4051BQ; DHVQFN-16-2.5X3.5MM

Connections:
!E!: J2.1, R1.1, U1.6 (!E!)
GND: C1.2, J1.9, J2.6, JP1.1, R1.2, U1.8 (GND)
S0: J2.4, U1.11 (S0)
S1: J2.3, U1.10 (S1)
S2: J2.2, U1.9 (S2)
VCC: C1.1, J1.10, J2.7, U1.16 (VCC), U1.EP (VCC)
VEE: J1.11, J2.8, JP1.2, U1.7 (VEE)
Y0: J1.8, U1.13 (Y0)
Y1: J1.7, U1.14 (Y1)
Y2: J1.6, U1.15 (Y2)
Y3: J1.5, U1.12 (Y3)
Y4: J1.4, U1.1 (Y4)
Y5: J1.3, U1.5 (Y5)
Y6: J1.2, U1.2 (Y6)
Y7: J1.1, U1.4 (Y7)
Z: J2.5, U1.3 (Z)

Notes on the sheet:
VCC-GND
VCC-VEE
Min Typ Max
2.0 5.0 10.0
v10
Jim Lindblom
JP1 shorts VEE to GND, if a bi-polar supply is not used. (Defaults closed.)
R1 keeps enable active (low). Pull !E! directly to VCC to disable the mux.
VCC VEE GND
10V 0V 0V
+5V -5V 0V
+2V -8V 0V
5V 0V 0V
Example Supplies
VCC/VEE/GND Range

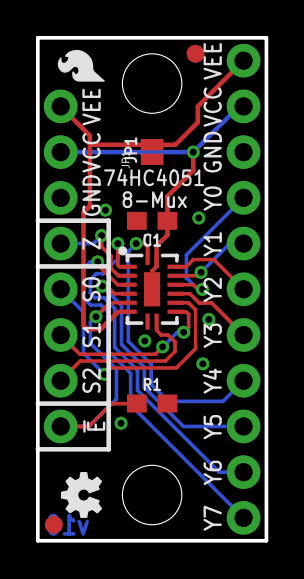
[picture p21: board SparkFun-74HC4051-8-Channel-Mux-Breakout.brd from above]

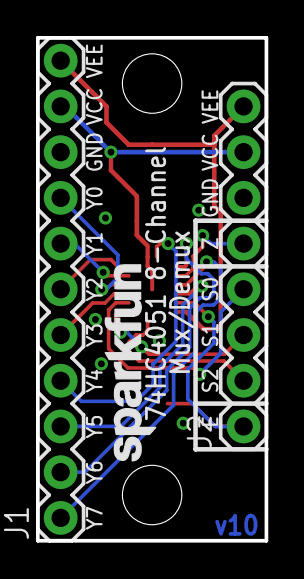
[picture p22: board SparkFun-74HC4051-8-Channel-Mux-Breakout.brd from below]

Board: 2 copper layers, 12.7 x 27.9 mm, 14 parts (3 on the bottom side), 16 nets.

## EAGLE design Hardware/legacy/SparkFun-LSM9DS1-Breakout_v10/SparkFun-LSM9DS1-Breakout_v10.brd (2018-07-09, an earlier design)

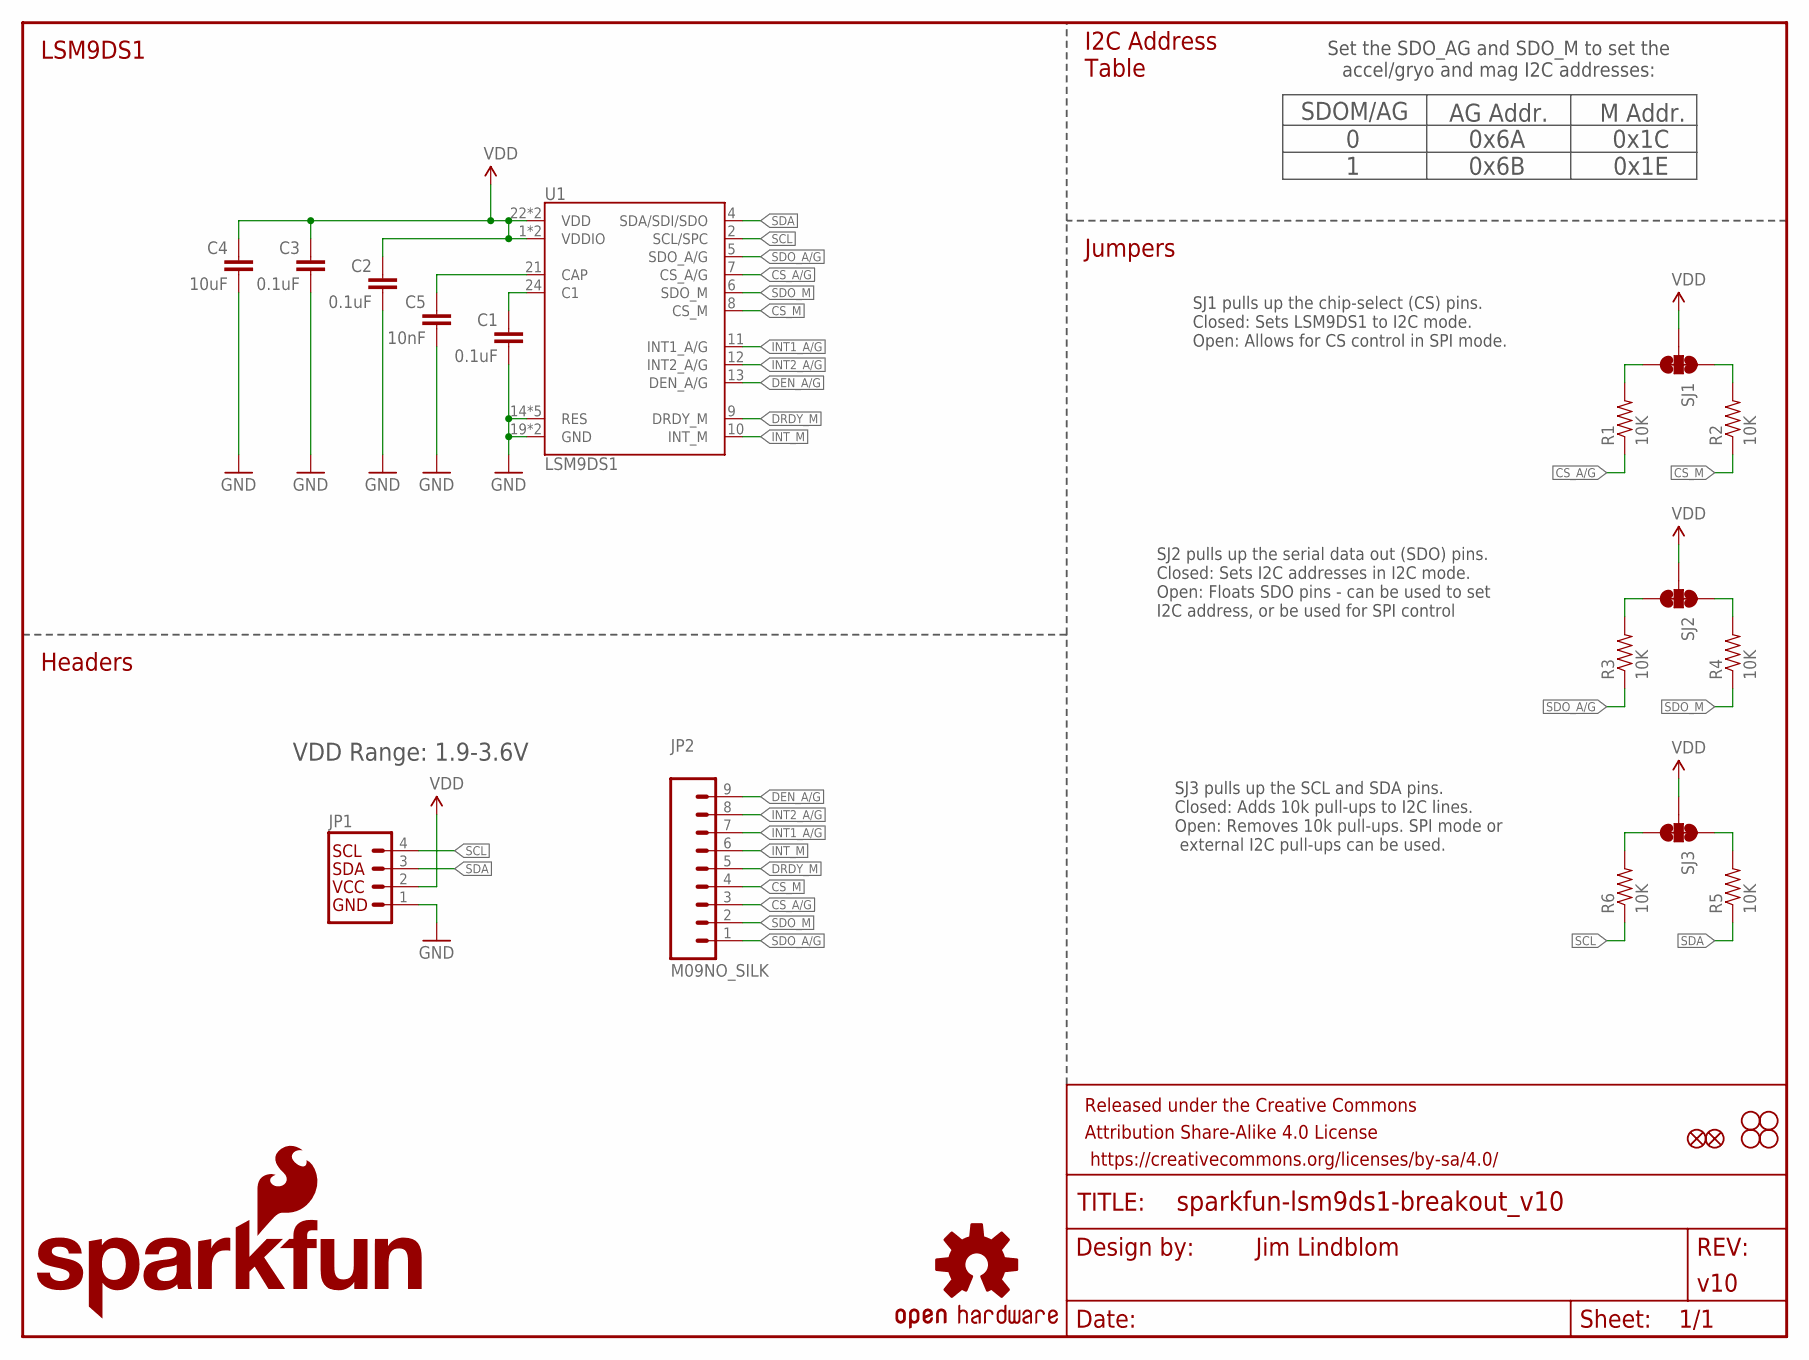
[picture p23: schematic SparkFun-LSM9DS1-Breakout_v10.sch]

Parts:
C1, C2, C3: 0.1uF; 0603-CAP
C4: 10uF; 0603-CAP
C5: 10nF; 0603-CAP
FID1, FID2: FIDUCIAL1X2; FIDUCIAL-1X2
FRAME1: FRAME-LETTER; CREATIVE_COMMONS
JP1: I2C_STANDARD_NO_SILK; 1X04_NO_SILK
JP2: M09NO_SILK; 1X09_NO_SILK
LOGO1: SFE_LOGO_NAME.1_INCH; SFE_LOGO_NAME_.1
LOGO2: SFE_LOGO_FLAME.2_INCH; SFE_LOGO_FLAME_.2
LOGO3: OSHW-LOGOS; OSHW-LOGO-S
R1, R2, R3, R4, R5, R6: 10K; 0603-RES
SJ1, SJ2, SJ3: JUMPER-PAD-3-NC_BY_TRACE; PAD-JUMPER-3-3OF3_NC_BY_TRACE_YES_SILK_FULL_BOX
STANDOFF1, STANDOFF2, STANDOFF3, STANDOFF4: STAND-OFF
U1: LSM9DS1; LGA24-8X4

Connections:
C1: C1.1, U1.24 (C1)
CAP: C5.1, U1.21 (CAP)
CS_A/G: JP2.3, R1.1, U1.7 (CS_A/G)
CS_A/G_PU: R1.2, SJ1.3
CS_M: JP2.4, R2.1, U1.8 (CS_M)
CS_M_PU: R2.2, SJ1.1
DEN_A/G: JP2.9, U1.13 (DEN_A/G)
DRDY_M: JP2.5, U1.9 (DRDY_M)
GND: C1.2, C2.2, C3.2, C4.2, C5.2, JP1.1, U1.14 (RES), U1.15 (RES), U1.16 (RES), U1.17 (RES), U1.18 (RES), U1.19 (GND), U1.20 (GND)
INT1_A/G: JP2.7, U1.11 (INT1_A/G)
INT2_A/G: JP2.8, U1.12 (INT2_A/G)
INT_M: JP2.6, U1.10 (INT_M)
SCL: JP1.4, R6.1, U1.2 (SCL/SPC)
SCL_PU: R6.2, SJ3.3
SDA: JP1.3, R5.1, U1.4 (SDA/SDI/SDO)
SDA_PU: R5.2, SJ3.1
SDO_A/G: JP2.1, R3.1, U1.5 (SDO_A/G)
SDO_A/G_PU: R3.2, SJ2.3
SDO_M: JP2.2, R4.1, U1.6 (SDO_M)
SDO_M_PU: R4.2, SJ2.1
VDD: C2.1, C3.1, C4.1, JP1.2, SJ1.2, SJ2.2, SJ3.2, U1.1 (VDDIO), U1.3 (VDDIO), U1.22 (VDD), U1.23 (VDD)

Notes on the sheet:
SDOM/AG
0x1C 0x1E
AG Addr.
0 1
M Addr.
0x6A 0x6B
Set the SDO_AG and SDO_M to set the accel/gryo and mag I2C addresses:
SJ1 pulls up the chip-select (CS) pins. Closed: Sets LSM9DS1 to I2C mode. Open: Allows for CS control in SPI mode.
SJ2 pulls up the serial data out (SDO) pins. Closed: Sets I2C addresses in I2C mode. Open: Floats SDO pins - can be used to set I2C address, or be used for SPI control
SJ3 pulls up the SCL and SDA pins. Closed: Adds 10k pull-ups to I2C lines. Open: Removes 10k pull-ups. SPI mode or external I2C pull-ups can be used.
Jumpers
I2C Address Table
LSM9DS1
Headers
VDD Range: 1.9-3.6V

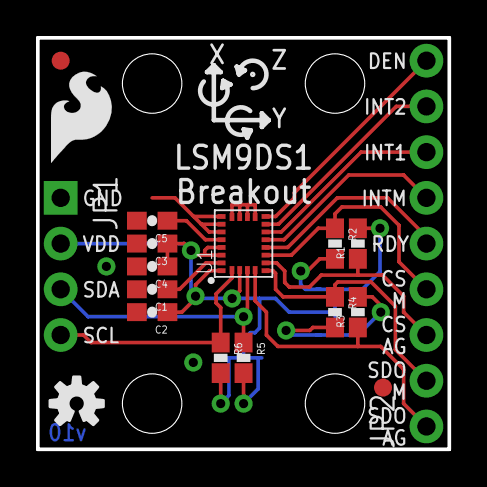
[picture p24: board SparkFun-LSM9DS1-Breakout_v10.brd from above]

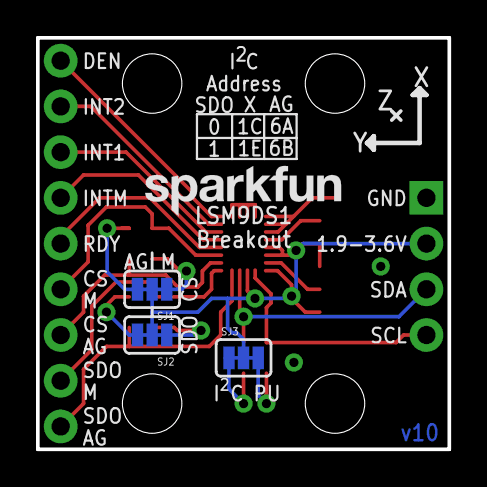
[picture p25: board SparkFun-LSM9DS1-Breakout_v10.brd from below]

Board: 2 copper layers, 22.9 x 22.9 mm, 27 parts (4 on the bottom side), 21 nets.

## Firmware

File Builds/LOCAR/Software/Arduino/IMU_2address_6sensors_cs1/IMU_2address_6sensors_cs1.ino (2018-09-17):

/*
   Obtain magnetic field vector using multiplexed LSM9DS1 IMU sensors.
   Obtained values take into account the magnetic field of the earth,
   and the immediately surrounding area by taking a baseline average for each axis
   and then subtracting each them from the readings to give a calibrated reading
   independent of the ambient magnetic field.

   AUTHOR                  : Edward Daniel Nichols
   LAST CONTRIBUTION DATE  : Nov. 6th, 2017, Year of Our Lord

   AUTHOR                  : Mohammad Odeh
   LAST CONTRIBUTION DATE  : Nov. 7th, 2017 Year of Our Lord

   CHANGELOG:-
    1- Both possible addresses for the IMUs are implemented.
    2- Calibration speed has significantly improved.
    3- All six sensors have been added.
    4- Implemented an EMA filter for smoothing data output.

    There is room to add more sensors.
*/

// Include required libraries
#include <Wire.h>
#include <SPI.h>
#include "SparkFunLSM9DS1.h"

// Define sensor address, for the setup.
#define LSM9DS1_M_HIGH                0x1E    // SDO_M on these IMU's are HIGH
#define LSM9DS1_AG_HIGH               0x6B    // SDO_AG on these IMU's are HIGH 
#define LSM9DS1_M_LOW                 0x1C    // SDO_M on these IMU's are LOW
#define LSM9DS1_AG_LOW                0x6B    // SDO_AG on these IMU's are HIGH [PINS NOT GROUNDED]***

// Useful defines.
#define CALIBRATION_INDEX             150     // Accounting for ambient magnetic fields
#define DECLINATION                   6.29    // Accounting for the Earth's magnetic field
#define BAUDRATE                      115200  // Serial communication baudrate
#define MUX_PIN                       10      // Multiplexer "Select pin"
#define DEBOUNCE                      1       // To ensure select pin voltage has enough time to settle.

// MUX lines are on these pins.
#define S0                            8
#define S1                            9
#define S2                            10
// S2 is grounded.
// MUX lines are selected in binary.
// For example, Y0 -> S0=LOW, S1=LOW, S2=LOW -> 000.

// Sensor Calibration variables: To store the averaged baseline values for each sensor.
double cal[6][3] = {0};

// Array that will house the smoothed sensor orientation adjusted readings, for printing.
// See the 'sensorOrientation()' definition.
double sens[6][3] = {0};

// Initialize two instances of the LSM object; one for each M_address.
LSM9DS1 high; //Odd sensors 1, 3, and 5
LSM9DS1 low;  //Even sensors 2, 4, and 6

// Call auxiliary functions library
#include "functions.h"

void setup() {
  // Start serial monitor.
  Serial.begin( BAUDRATE );

  // Initialize the necessary MUX selection pins.
  pinMode(S0, OUTPUT);
  pinMode(S1, OUTPUT);
  pinMode(S2, OUTPUT);
  digitalWrite(S2, LOW);

  for (int whichPair = 1; whichPair <= 3; whichPair++) {

    pairSelect(whichPair);    // Switch between all sensor pairs
    setupIMU();               // Setup IMUS

    //Initialize the sensors, and print error code if failure.
    if ( !high.begin() || !low.begin() ) {
      Serial.print( F("Failed to communicate with LSM9DS1 in pair:") );
      Serial.println(whichPair);
      while (1);
    } else {

      Serial.println( F("Calibrating, please wait.") );
      delay(25);
      //Calibration function:
      double hold[6] = {0};
      for (int i = 0; i < CALIBRATION_INDEX; i++) {

        //Declaring an index, to make it easier to assign values to/from the correct sensor.
        int n_hi = (whichPair - 1) * 2;
        int n_lo = (2 * whichPair) - 1;

        //Wait until sensors are available.
        delay(10);
        while ( !low.magAvailable() && !high.magAvailable() );

        high.readMag();                 // Take readings (High sensors)
        low.readMag();                  // Take readings (Low sensors)

        orientRead(whichPair);          //Reorient readings and push to the array

        hold[0] += sens[n_hi][0];       // Populate temporary hold array
        hold[1] += sens[n_hi][1];       // for the HIGH sensors.
        hold[2] += sens[n_hi][2];       // ...

        hold[3] += sens[n_lo][0];       // Populate temporary hold array
        hold[4] += sens[n_lo][1];       // for the LOW sensors.
        hold[5] += sens[n_lo][2];       // ...

        if ( i == CALIBRATION_INDEX - 1) {
          cal[n_hi][0] = hold[0] / CALIBRATION_INDEX;   // Compute the calibration (BASE)
          cal[n_hi][1] = hold[1] / CALIBRATION_INDEX;   // values for the High sensors
          cal[n_hi][2] = hold[2] / CALIBRATION_INDEX;   // ...

          //Computing, finally, the actual calibration value for the Low sensor.
          cal[n_lo][0] = hold[3] / CALIBRATION_INDEX;   // Compute the calibration (BASE)
          cal[n_lo][1] = hold[4] / CALIBRATION_INDEX;   // values for the Low sensors
          cal[n_lo][2] = hold[5] / CALIBRATION_INDEX;   // ...

        };
      };

      Serial.print( F("Calibration success for pair: ") );
      Serial.println(whichPair);
    };
  };
};

void loop() {
  Serial.print("<");          // Start of data specifier

  for (int whichPair = 1; whichPair <= 3; whichPair++) {
    pairSelect(whichPair);    // Switch between all sensor pairs

    //Wait until the sensors are available.
    while (!low.magAvailable() && !high.magAvailable() );

    high.readMag();           // Take readings (High sensors)
    low.readMag();            // Take readings (Low sensors)

    orientRead(whichPair);    //Reorient readings and push to the array
  }

  //When all of the values have been collected, print them all at once!
  //Adjusting for the calibration baseline!
  for (int i = 0; i < 6; i++) {
    for (int j = 0; j < 3; j++) {
      Serial.print(sens[i][j] - cal[i][j], 5);
      //delay(2);
      if (i == 5 && j == 2) {
        //Serial.println();
        continue;
      } else {
        Serial.print(", ");
      };
    };
  };

  Serial.println(">");
};

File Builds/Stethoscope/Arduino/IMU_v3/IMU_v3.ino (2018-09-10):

/*
 *  Obtain magnetic field vector using multiplexed LSM9DS1 IMU sensors.
 *  Obtained values take into account the magnetic field of the earth
 *  and the immediate surrounding area and SUBTRACTS them from the readings
 *  to give a calibrated reading independent of the surrounding magnetic field.
 *
 *  AUTHOR                  : Edward Daniel Nichols
 *  LAST CONTRIBUTION DATE  : Sep. 29th, 2017, Year of Our Lord
 *
 *  AUTHOR                  : Mohammad Odeh 
 *  LAST CONTRIBUTION DATE  : Oct. 26th, 2017 Year of Our Lord
 *
 *  CHANGELOG:-
 *   1- Use 2 I2C addresses for communicating with sensors
 *                (Improves data output rate)
 */

// Include required libraries
#include <Wire.h>
#include <SPI.h>
#include <SparkFunLSM9DS1.h>

// Define important constants
#define LSM9DS1_M_HIGH        0x1E    // Would be 0x1C if SDO_M is LOW
#define LSM9DS1_AG_HIGH       0x6B    // Would be 0x6A if SDO_AG is LOW
#define LSM9DS1_M_LOW         0x1C    // SDO_M on these IMU's are LOW
#define LSM9DS1_AG_LOW        0x6B    // SDO_AG on these IMU's are HIGH [PINS NOT GROUNDED]***
#define CALIBRATION_INDEX     50      // Accounting for ambient magnetic fields
#define BAUDRATE              115200  // Serial communication baudrate
#define NPINS                 3       // Number of select pins
#define NSENS                 6       // Number of sensors
#define NPAIR                 3       // Number of pairs
#define NAXES                 3       // Number of axes

LSM9DS1 imuHIGH;                      // Instantiate sensors associated with I2C address of HIGH
LSM9DS1 imuLOW;                       // Instantiate sensors associated with I2C address of LOW

byte Sx_pin[3]  = {8, 9, 10};         // Select pins: {S0, S1, S2}

// Calibration (BASE) readings
static double imu_BASE[NSENS][NAXES] =  { {0, 0, 0},    //  {1x, 1y, 1z}
                                          {0, 0, 0},    //  {2x, 2y, 2z}
                                          {0, 0, 0},    //  {3x, 3y, 3z}
                                          {0, 0, 0},    //  {4x, 4y, 4z}
                                          {0, 0, 0},    //  {5x, 5y, 5z}
                                          {0, 0, 0} };  //  {6x, 6y, 6z}

// Enumerate sensor states ( 0==sensor1, 1==sensor2, ..., n==sensor(n+1) )
enum State { SEN_ERR, SEN_OK };
State sensorState[NSENS]  = { };      // Is the sensor detected and working?

void setup() {
  Serial.begin( BAUDRATE );           // Start serial monitor

  pinMode( 13, OUTPUT );              // Turn LED ON to know
  digitalWrite( 13, HIGH );           // Teensy ain't dead

  for ( byte i = 0; i < NPINS; i++ ) {
    pinMode( Sx_pin[i], OUTPUT );     // Set "Select Pins" as output
  }

  // Initialize sensors and load settings
  for (byte i = 0; i < NPAIR; i++) {
    sensorPairSelect(i);              // Switch between sensors
    setupIMU();                       // Setup IMUs
    calibrateIMU(HIGH, i);            // Calibrate Sensors
    calibrateIMU(LOW , i);            // Calibrate Sensors
  } Serial.println( F("Success.") );  // SUCCESS!
}

void loop() {

  // IMU readings (RAW)
  static double imu_RAW_X = 0;
  static double imu_RAW_Y = 0;
  static double imu_RAW_Z = 0;

  
  Serial.print("<");                                                // Start of data specifier

  // Obtain readings from ALL sensors
  for (byte i = 0; i < NPAIR; i++) {                                // Loop over the sensor pairs

    if(sensorState[2*i] == SEN_OK && sensorState[2*i+1] == SEN_OK) {// Set Sensor IFF it was INITIALIZED
      sensorPairSelect(i);                                          // Loop over sensors
      while ( !imuHIGH.magAvailable() && !imuLOW.magAvailable() );  // Check if sensor is ready

      // ------------------------------ SENSORS ON HIGH I2C ADDRESS ------------------------------
      
      imuHIGH.readMag();                                            // Do readings
      imu_RAW_X = double( imuHIGH.calcMag(imuHIGH.mx) );            //
      imu_RAW_Y = double( imuHIGH.calcMag(imuHIGH.my) );            // Store in temporary variable
      imu_RAW_Z = double( imuHIGH.calcMag(imuHIGH.mz) );            //

      // Subtract BASE readings from RAW readings to get CALIBRATED readings
      Serial.print(( imu_RAW_X - imu_BASE[2*i][0] ), 5);            // Print X readings to Serial
      Serial.print(", ");                                           // Comma delimit output
      Serial.print(( imu_RAW_Y - imu_BASE[2*i][1] ), 5);            // Print readings to Serial
      Serial.print(", ");                                           // Comma Y delimit output
      Serial.print(( imu_RAW_Z - imu_BASE[2*i][2] ), 5);            // Print Z readings to Serial
      Serial.print(", ");                                           // Comma Z delimit output

      // ------------------------------ SENSORS ON LOW I2C ADDRESS -------------------------------
      
      imuLOW.readMag();                                             // Do readings
      imu_RAW_X = double( imuLOW.calcMag(imuLOW.mx) );              //
      imu_RAW_Y = double( imuLOW.calcMag(imuLOW.my) );              // Store in temporary variable
      imu_RAW_Z = double( imuLOW.calcMag(imuLOW.mz) );              //

      // Subtract BASE readings from RAW readings to get CALIBRATED readings
      Serial.print(( imu_RAW_X - imu_BASE[2*i+1][0] ), 5);          // Print X readings to Serial
      Serial.print(", ");                                           // Comma delimit output
      Serial.print(( imu_RAW_Y - imu_BASE[2*i+1][1] ), 5);          // Print readings to Serial
      Serial.print(", ");                                           // Comma Y delimit output
      Serial.print(( imu_RAW_Z - imu_BASE[2*i+1][2] ), 5);          // Print Z readings to Serial
    }

    if(i != NPAIR - 1) Serial.print(", ");                              // Comma delimit output
  }
  Serial.print(">\n");                                              // End of data specifier
}

// =========================    Setup IMU       ========================
void setupIMU() {

  // ---------------------------------------- HIGH IMU Setup ---------------------------------------
  
  imuHIGH.settings.device.commInterface = IMU_MODE_I2C;   //
  imuHIGH.settings.device.mAddress      = LSM9DS1_M_HIGH; // Load IMU settings
  imuHIGH.settings.device.agAddress     = LSM9DS1_AG_HIGH;//

  imuHIGH.settings.gyro.enabled         = false;          // Disable gyro
  imuHIGH.settings.accel.enabled        = false;          // Disable accelerometer
  imuHIGH.settings.mag.enabled          = true;           // Enable magnetometer
  imuHIGH.settings.temp.enabled         = true;           // Enable temperature sensor

  imuHIGH.settings.mag.scale            = 16;             // Set mag scale to +/-12 Gs
  imuHIGH.settings.mag.sampleRate       = 7;              // Set OD rate to 80Hz
  imuHIGH.settings.mag.tempCompensationEnable = true;     // Enable temperature compensation (good stuff!)

  imuHIGH.settings.mag.XYPerformance    = 3;              // 0 = Low || 1 = Medium || 2 = High || 3 = Ultra-high
  imuHIGH.settings.mag.ZPerformance     = 3;              // Ultra-high performance

  imuHIGH.settings.mag.lowPowerEnable   = false;          // Disable low power mode
  imuHIGH.settings.mag.operatingMode    = 0;              // 0 = Continuous || 1 = Single || 2 = OFF

  // ---------------------------------------- LOW IMU Setup ----------------------------------------

  imuLOW.settings.device.commInterface = IMU_MODE_I2C;    //
  imuLOW.settings.device.mAddress      = LSM9DS1_M_LOW;   // Load IMU settings
  imuLOW.settings.device.agAddress     = LSM9DS1_AG_LOW;  //

  imuLOW.settings.gyro.enabled         = false;           // Disable gyro
  imuLOW.settings.accel.enabled        = false;           // Disable accelerometer
  imuLOW.settings.mag.enabled          = true;            // Enable magnetometer
  imuLOW.settings.temp.enabled         = true;            // Enable temperature sensor

  imuLOW.settings.mag.scale            = 16;              // Set mag scale to +/-12 Gs
  imuLOW.settings.mag.sampleRate       = 7;               // Set OD rate to 80Hz
  imuLOW.settings.mag.tempCompensationEnable = true;      // Enable temperature compensation (good stuff!)

  imuLOW.settings.mag.XYPerformance    = 3;               // 0 = Low || 1 = Medium || 2 = High || 3 = Ultra-high
  imuLOW.settings.mag.ZPerformance     = 3;               // Ultra-high performance

  imuLOW.settings.mag.lowPowerEnable   = false;           // Disable low power mode
  imuLOW.settings.mag.operatingMode    = 0;               // 0 = Continuous || 1 = Single || 2 = OFF

}
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

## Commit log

2018-06-28 Initial arduino code
2018-06-28 Python side
    [SP_PH02_Torso (ASCII).stl, SP_PH02_Torso_Inverted (ASCII).stl]
2018-07-09 Fritzing-style PCB. Next iteration PCB, in progress.
    [SparkFun-74HC4051-8-Channel-Mux-Breakout.brd, SparkFun-74HC4051-8-Channel-Mux-Breakout.sch, SparkFun-LSM9DS1-Breakout_v10.brd, SparkFun-LSM9DS1-Breakout_v10.sc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]
2018-07-12 PCB for the magneto board is complete. Send .brd file to Oshpark.
    [magnetoV3.0.brd, magnetoV3.0.sch]
2018-07-18 Added directories for documentation of housing designs, other parts
2018-07-19 1- Move to MQTT 2- Store calibration offsets in EEPROM 3- No need to perform a hard-reset on failure
2018-09-10 Port original work from Stethoscope repo
    [K Values for Multiple Magnets.xlsx, SP_PH02_Torso (ASCII).stl, SP_PH02_Torso (BIN).stl, SP_PH02_Torso.obj]
2018-09-14 Created a directory for sensor libraries to be referenced or copied into the working Arduino scripts
2018-09-17 Created a directory called "builds," were entire prototypes will be consolidated and documented
    [6MAG_arduino_plate.stl, SparkFun-74HC4051-8-Channel-Mux-Breakout.brd, SparkFun-74HC4051-8-Channel-Mux-Breakout.sch, SparkFun-LSM9DS1-Breakout_v10.brd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]
2018-09-17 Moved the software corresponding to the 6 magnetometer array ring prototype to the corresponding build folder. Also modified library references within the Arduino script to allow compilation without 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
2018-09-17 The latest build needed a switch in digital pins due to a hardware malfunction of the arduino in use. The reference pins should be 10, 9, and 8
2018-09-17 Began working on a bash script that installs all required packages for the proper operation of the build/prototype.
2018-09-18 Modified the python scripts to work with a linux-based computer or control system. In our case, a chromebook running the GalliumOS linux distribution.
2018-09-24 Completed a working version of the plotting script. This made us realize that the graphics performance of the chromebooks may not be enough for the live calculation and plotting.
    [SP_PH02_Torso (ASCII).stl, SP_PH02_Torso (BIN).stl, SP_PH02_Torso.obj]
2018-09-25 Created a branch and a python script to generate a gcode that forces a 3D printer to follow a specific path
2018-09-25 Created a working g-code generator to force any printer to follow a 3D path. Need to offset the paths to not be centered around 0. Printers coordinate system are positive always.
2018-09-27 Added the LAPARO directory to the Builds folder.
    [6MAG_arduino_plate.stl, SP_PH02_Torso (ASCII).stl, SP_PH02_Torso (BIN).stl, SP_PH02_Torso.obj]
2018-10-06 Added the speed capability to the gcode generator function. Also generated three g-codes for helical motion at three different speeds. Simulated them but have yet to test on the printer.
2018-10-09 Added python implementation to the builds directory
    [K Values for Multiple Magnets.xlsx]
2018-10-09 Automate installation of dependencies on Windows
    [SP_PH02_Torso (ASCII).stl, SP_PH02_Torso (BIN).stl, SP_PH02_Torso.obj]
2018-10-11 Added a version of the arduino script to control a given/input number of sensors, rather than relying on a hardcoded value.
2018-10-11 Corrected number of sensors and data array to be more flexible
2018-10-11 Created a 4MAG directory within the builds folder. 4-sensor-arrays are planned as prototypes.
2018-10-11 Began modifying the python position tracking script to fit the 4-sensor array. Moved the entire development to python 3, on windows for now.
2018-10-26 Data collection
    [Point Accuracy Data.xlsx]
2018-11-01 Completed a working random walk with intervals defined in milliseconds
2018-11-01 Added the enable/disable steppers feature in the motion random walk code
2018-11-05 Tested the random walk code a little further and realized that the current version continues on a random path which could, if unlucky/lucky enough, past input limits. The next version will support re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
2018-11-06 Created and tested a version of the center random walk gocde generation process featuring retraction. Retraction consists on the return of the magnet holder to the center/origin of the printer (start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
2018-11-19 Began working on the daisypair prototype of the PC-board/breakout
    [daisypair.fzz]
2018-11-19 Tested ground fill
    [daisypair.fzz]
2018-11-19 Finihsed the daisypair design/model
    [daisypair.fzz]
2018-11-19 Exported fabrication files for all versions of the daisy pair modules. Started a BOM and purchase order.
    [Component Order 11192018.xlsx, daisypair --inv.fzz, daisypair --jst.fzz, daisypair_contour.gm1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]
2018-11-19 Updated BOM
    [Component Order 11192018.xlsx]
2018-11-19 Finished the daisychain module design
    [daisychain.fzz]
2018-11-19 Saved latest changes to the daisychain module
    [daisychain.fzz]
2018-11-19 Fixed issues with the sodler pads or smd jumpers. Need to check these tolerances in the other designs.
    [daisychain --xs.fzz, daisychain --xs_contour.gm1, daisychain --xs_copperBottom.gbl, daisychain --xs_copperTop.gtl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]
2018-11-20 Completed the extra-small version of the IMU hubs for the daisy chain prototype.
    [daisychain --xs --wLED.fzz, daisychain --xs.fzz, daisychain --xs_contour.gm1, daisychain --xs_copperBottom.gbl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]
2018-11-20 Corrected missing SCL connection on the extra small version of the IMU modules
    [daisychain --xs.fzz, daisychain --xs_copperBottom.gbl, daisychain --xs_copperTop.gtl, daisychain --xs_maskTop.gts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]
2018-11-20 Updated the version of the hub for the xs version of the IMU modules. The hub model should serve all of the versions to be made. Needs more work!!!
    [daisychain_hub --xs.fzz]
2018-11-20 Currently working on the pi wing/hat adapter for the multiplexing.
    [daisychain_hub --pi.fzz, daisychain_hub --pi_PCB1_854635090_contour.gm1, daisychain_hub --pi_PCB1_854635090_copperBottom.gbl, daisychain_hub --pi_PCB1_85463509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]
2018-11-20 Added thin wire connections to the Locar PCB design
    [daisychain_hub --pi.fzz]
2018-11-20 Exported fabrication files for the pi hub PCB
    [daisychain_hub --pi.fzz, daisychain_hub --pi_copperBottom.gbl, daisychain_hub --pi_copperTop.gtl, daisychain_hub --pi_maskBottom.gbs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]
2018-11-20 Added pd3d logo and label for the finished part. Currently working on auxiliary pins for additional sensors, power and ground.
    [daisychain_hub --pi.fzz]
2018-11-21 Began working on a version of the IMU board that has THT LEDs for signaling data line number and, thus, device pair.
    [daisychain --xs --wLED.fzz]
2018-11-21 Finished the latest version of the extra small daisy chain module, which includes LEDs to verify the SDA line in use.
    [daisychain --xs --wLED.fzz, daisychain --xs --wLED_contour.gm1, daisychain --xs --wLED_copperBottom.gbl, daisychain --xs --wLED_copperTop.gtl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]
2018-11-21 Created a legacy folder and placed obsolete or old versions of the daisychain boards
    [daisychain --xs.fzz, daisychain --xs_contour.gm1, daisychain --xs_copperBottom.gbl, daisychain --xs_copperTop.gtl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]
2018-11-21 Finished pi wing hub project, added final features and exported manufacturing files.
    [Component Order 11192018.xlsx, daisychain_hub --pi.fzz, daisychain_hub --pi_PCB1_854635090_contour.gm1, daisychain_hub --pi_PCB1_854635090_copperBottom.gbl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]
2018-12-14 Updated latest changes to the board
    [daisychain --xs --wLED.fzz, daisychain --xs --wLED_copperTop.gtl, daisychain_hub --pi.fzz, daisychain_hub --pi_copperBottom.gbl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]
2018-12-14 Created a working BOM for LOCAR
    [LOCAR BOM 12142018.xlsx]
2018-12-20 Re-structure directories to refer to the LOCAR prototype and the daisyhub design
    [6MAG_arduino_plate.stl, Component Order 11192018.xlsx, LOCAR BOM 12142018.xlsx, Point Accuracy Data.xlsx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]
2018-12-20 Created a new version of the daisyhub design. Removed the LEDs and moved the SDA solder jumpers to the bottom of the board.
    [daisychain --v2.fzz, daisychain --v2_contour.gm1, daisychain --v2_copperBottom.gbl, daisychain --v2_copperTop.gtl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]
2018-12-20 Changed name of the latest file to daisyhub instead of chain
    [daisyhub --v2.fzz]
2018-12-20 Began working on a version of the daisyhub design that allows for up to 14 pairs of sensors.
    [daisyhub --v3.fzz]
2019-02-21 Restructure the windows directory
    [Point Accuracy Data.xlsx, SP_PH02_Torso (ASCII).stl, SP_PH02_Torso (BIN).stl, SP_PH02_Torso.obj]
2019-02-21 Updated BOMs
    [LOCAR BOM 02212019.xlsx, LOCAR BOM 02222019.xlsx]
2019-02-28 Added the power supply PCB designed by MB
    [psupply --v1.fzz]
2019-02-28 Created gerber files for the PCBs
    [LOCAR BOM 02282019.xlsx, daisychain --v2_copperBottom.gbl, daisychain --xs --v2_contour.gm1, daisychain --xs --v2_copperTop.gtl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]
2019-02-28 Changed the number of sensors to be used, size of the array.

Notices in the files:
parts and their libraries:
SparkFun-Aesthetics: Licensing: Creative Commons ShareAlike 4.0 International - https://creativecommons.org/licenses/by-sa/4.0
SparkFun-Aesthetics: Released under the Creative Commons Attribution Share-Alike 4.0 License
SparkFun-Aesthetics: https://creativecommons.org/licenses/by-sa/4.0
